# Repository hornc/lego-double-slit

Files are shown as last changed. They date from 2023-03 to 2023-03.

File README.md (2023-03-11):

# LEGO Double Slit Experiment

This repo contains build instructions for a LEGO rig to conduct the famous [double-slit experiment](https://wikipedia.org/wiki/Double-slit_experiment),
first performed by [Thomas Young](https://wikipedia.org/wiki/Thomas_Young_(scientist)) in 1801, which demonstrates both the particle and wave behaviour of light.

It uses a cheap laser diode as the light source, and everyday white printer paper (80gsm) hand cut with an x-acto style craft blade for the slitted plate.

## Motivation

How to convincingly and reliably block one slit at a time (a slit toggle) during a single run of a double-slit experiment?

Rather than setting up two different experiments to show the difference, I wanted to have something stable enough to be toggled by
someone unfamiliar with the equipment or the experiment so they could see directly and hands-on the effect of toggling the slit openings.

The rig needed to be robust enough to handle the experiment surface (i.e. table) being bumped while retaining calibration, and cope with being bumped itself, picked up while
operating, and re-positioned or angled slightly with the laser operating (don't point lasers at people!), and still exhibit togglable slit interference.

* I wanted something that could be set up easily within <5 minutes, so if a visitor casually said "I've always wanted to perform the double-slit experiment", I could say I had one sitting in a box, and we could just get it and be done in minutes.
* Something somewhat portable to potentially demonstrate in other locations, with <5 min set up also. Currently the power-supply is the challenge, but a battery pack would suffice. (Ideally this would be made of LEGO too).

The current rig does need to be calibrated once before operating. The slit-plate position and angle needs to be aligned precisely with the laser pointer, and this can rely on 'twisting' and
partially connecting some of the LEGO studs in the rig. Cutting the slits freehand seems to be the quickest way to get a usable result, and cheap laser diodes don't necessarily point straight either.

Fortunately the precise LEGO joints allow them to be partially connected and still retain a decent mechanical stability that should last the duration of an experiment.

The rig will most likely need to be re-calibrated between runs, and I'd recommend cutting a fresh slit-plate each time anyway. The relatively thin paper tends to bend and lose definition with handling.

This started as a mock-up to model something which could be 3D printed, but the basic design worked well enough for me to run with it.

The initial design goal of having either slit togglable has not been realised. There is a large gap between the two shutters that cannot block the entire laser beam, but by playing with the LEGO connections
it was simple enough to find a position that clearly blocked at least one slit with one slider pushed all the way in, in a way that didn't require precise handling of the slider, after initial calibration.

* 'Expert' calibration is performed once (somewhat efficiently) on setup by the experimenter
* Slits can then be toggled at will by others, who don't need to be *too* careful about breaking the calibration

Obviously the equipment is still sensitive, and should not be dropped or hit,
but previously I've done this in a way that someone nearby moving, tugging a wire, leaning on the table, or breathing too much breaks the setup and it takes 30 minutes plus to recreate the working conditions (this may be *slight* exaggeration).

## Non-LEGO parts

Only two non-LEGO parts are required.

* A cheap low-powered laser diode. (6mm diameter)
* A hand cut piece of 80gsm paper for the plate.

I powered my laser diode (red, 650nm) directly from a bench power-supply with no extra circuitry other than the built-in current limiting resistor. This is not the best way to use a laser diode, and there is a risk the diode could fail, but it's simple and often cheap consumer devices using these don't have decent protection circuitry either, and they work well enough. I bought a bag of 20 from eBay -- these are the unbranded 6mm brass housed ones which come bulk in either 5V or 3V configuration (either will work here). They all seem to have one red and one blue wire for power. The most important attribute is the 6mm barrel size to fit with the LEGO. Use and power your lasers at your own risk.

Paper slit-plate:  A small rectangle, roughly 25 x 40mm of 80gsm paper, with the slits between 3-4mm long (not critical, it's hard to make shorter cuts by hand, whatever works). They should be as parallel as possible, and the crucial part is that they are *close together*. 0.5mm (half a millimeter) works well. I found it difficult to measure in advance, so cutting as close as possible without tearing the paper using a sharp x-acto type paper-craft knife works. Scissors or box-cutter knives may not be fine enough for this. If your resulting slits are anywhere close to 0.5mm apart, it will work.
The paper weight of 80gsm is about as low as it can be -- thinner paper will cause problems. I didn't want the paper too thick ensuring the slits were clean, and as '2D' as possible.
At this scale, thicker paper might form a tunnel rather than a slit. Slightly thicker paper *may* work, and could last longer, but I have not yet tried it.

I modelled these parts exactly as possible using OpenSCAD, and converted them using the `stl2dat` tool to include them in the LeoCAD model.

## Results

Design:

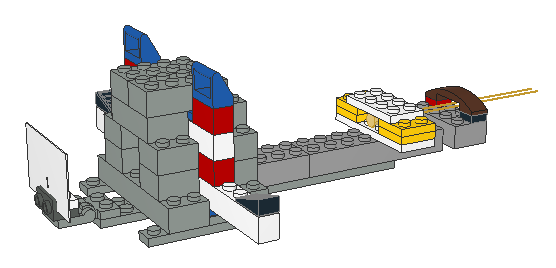
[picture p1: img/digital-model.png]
Digital model


Build, with a 6 stud wide, 6 brick + 1 plate high base for stability:
(some of this LEGO happens to be old, please excuse the dirt)

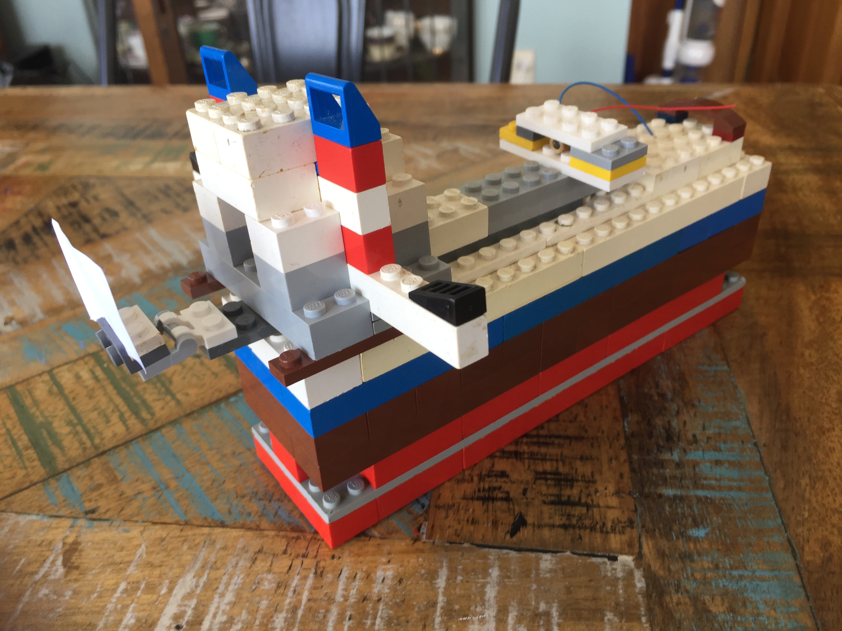
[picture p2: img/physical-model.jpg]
Physical model


Double slit interference pattern using this rig:

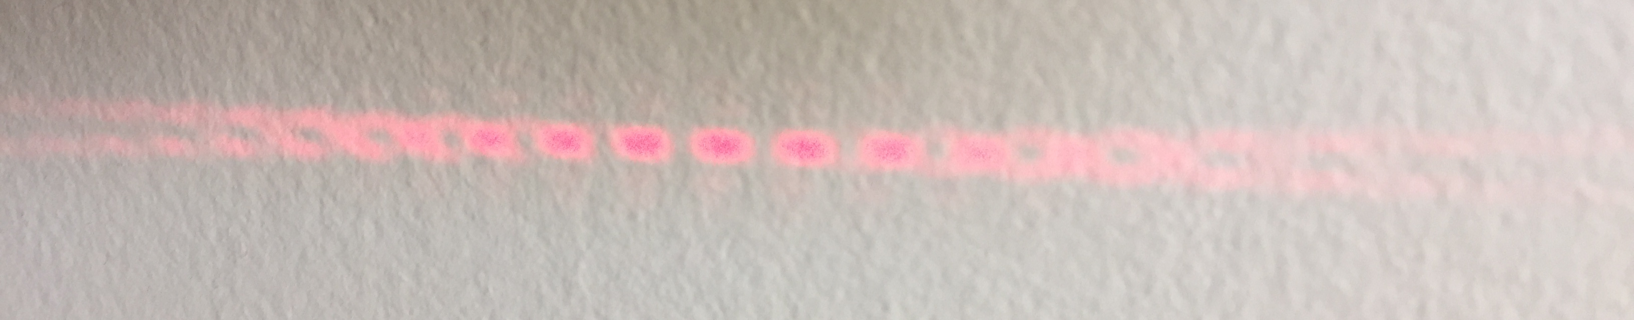
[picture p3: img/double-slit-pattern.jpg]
Double slit interference pattern


Single slit pattern:

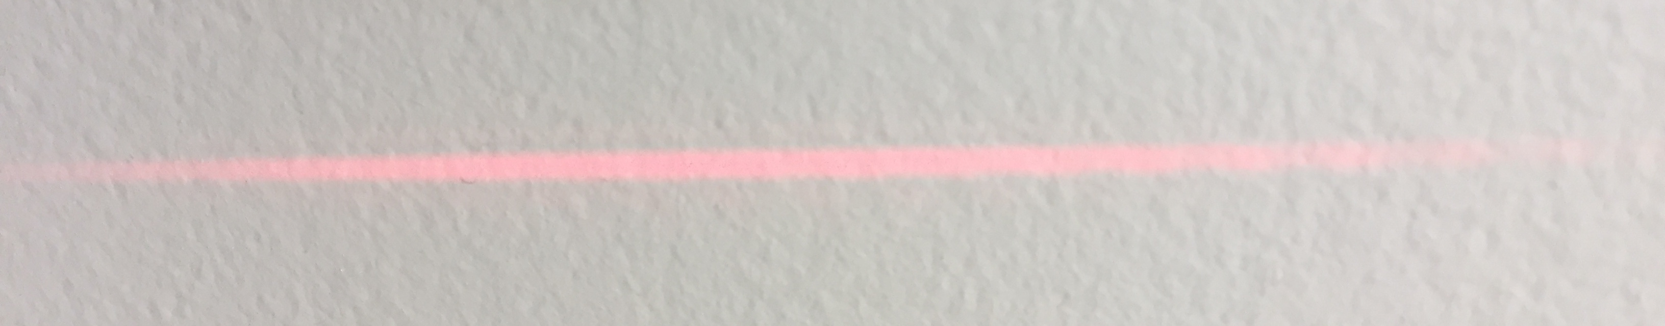
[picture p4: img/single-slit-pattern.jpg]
Single slit pattern


The above photos were taken indoors during the day, with no effort to limit surrounding light. The intent is that this is easy to set up, and the results are still clear.

## Software tools used

* [LeoCAD](https://www.leocad.org/) for LEGO modelling
* [OpenSCAD](https://openscad.org/) for non-LEGO parts and .stl conversion
* [stl2dat](https://github.com/ondratu/stl2dat-cp) for converting .stl to LDraw models for use in LeoCAD

## Extensions
TODO:
* Quantum eraser version with polarisers: https://doi.org/10.1038%2Fscientificamerican0507-90

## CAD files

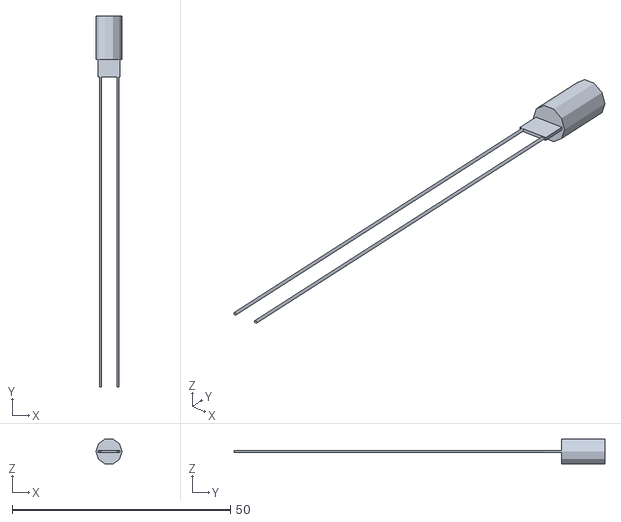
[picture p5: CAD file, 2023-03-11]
models/02_stl/laser-diode.stl
6.00 x 85.0 x 5.71

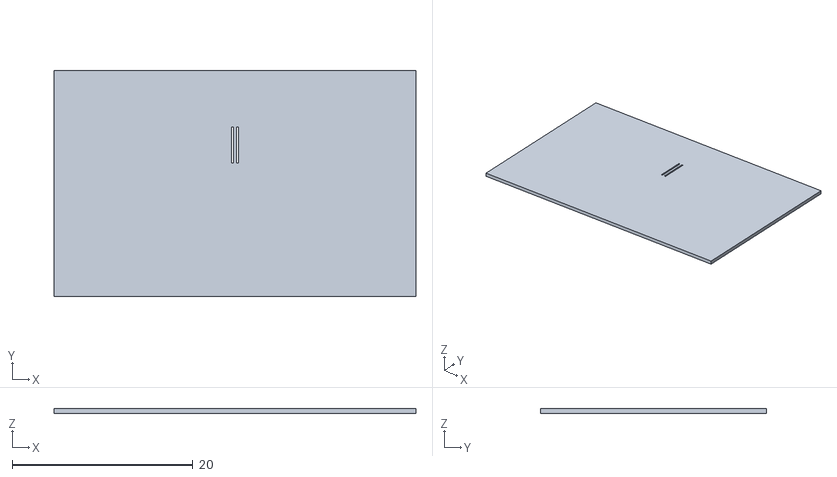
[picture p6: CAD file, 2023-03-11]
models/02_stl/double-slit.stl
40.0 x 25.0 x 0.5

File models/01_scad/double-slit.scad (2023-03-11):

module slit(t) {
    translate(t){
        rotate([0, 90, 0])  
            cube(size = [4, 4, 0.2], center = true);
    }
}



translate([0, 0, 0]) {
difference() {
    cube(size = [40, 25, 0.5], center = true);
    slit([0.27, 4.25, 0]);
    slit([-0.27, 4.25, 0]);

}}

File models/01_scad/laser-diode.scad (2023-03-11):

rotate([90, 0, 0]) {
  cylinder(h=10, d=6, center=true);
  translate([0, 0, 7]) {
      cube([5, 0.5, 4], center=true);
  } 
  translate([2, 0, 0]) {
      cylinder(h=80, d=0.5);
  }
  translate([-2, 0, 0]) {
      cylinder(h=80, d=0.5);
  }
}
